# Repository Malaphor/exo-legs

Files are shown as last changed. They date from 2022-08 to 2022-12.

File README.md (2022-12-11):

# The Exoskeleton Project

## Overview

This project is a lower limb exoskeleton with 6 active joints. Its built with 3D printed and off-the-shelf parts. The aim is to get a basic, robust platform up and running for a comparatively low cost so that anyone that wants to can build it, use it and modify it however they wish. The exoskeleton is controlled with a [Teensy 4](https://www.pjrc.com/teensy/) and [ODrive 3.6](https://odriverobotics.com/shop/odrive-v36).

Requires [ODriveTeensyCAN](https://github.com/Malaphor/ODriveTeensyCAN) and [FlexCAN_T4](https://github.com/tonton81/FlexCAN_T4).

## Building

In the Documentation folder you will find assembly instructions and reference material for each of the parts required to build this project. There are separate folders for CAD files and STL files. The STL files are ready to print while the CAD files are there if you wish to modify any of the parts. Some off-the-shelf parts will need to be modified or adjusted to fit. For example, you may need to sand the inside of a bearing to fit around a motor or cut the aluminum extrusion to a specific length.

## Code

There are 3 subfolders in the Code folder. The code that runs on the Teensy is the brains of the exoskeleton. It handles gait, communication with motor controllers and sensors and also transfers data to the GUI. There is modified ODrive firmware that you'll need to flash to your ODrives to get voltage feedback from each joint potentiometer and to read some of the error flags in the heartbeat CAN message. Finally, the 3rd folder contains code for the GUI. This part is written in [Processing](https://processing.org/) and meant to be portable to run on whichever system you're using to control the exoskeleton, whether it be a tablet or desktop or something else.

# Mechanical Design

There are 6 active joints, 1 for each hip, knee and ankle. All of the joint actuators are designed to be extremely similar so once you get one joint working you can just print 5 more. The motor used here is a GARTT ML5210 brushless DC motor coupled to a size 17 120:1 strain wave gear (this is the most expensive part). This pair allows for up to 35Nm nominal torque and much more instantaneous torque. Both motor and gear are supported by large deep groove ball bearings and sandwiched between 3D printed parts. Between each joint and around the lower back are pieces of 20x40 aluminum extrusion that have been cut to length.

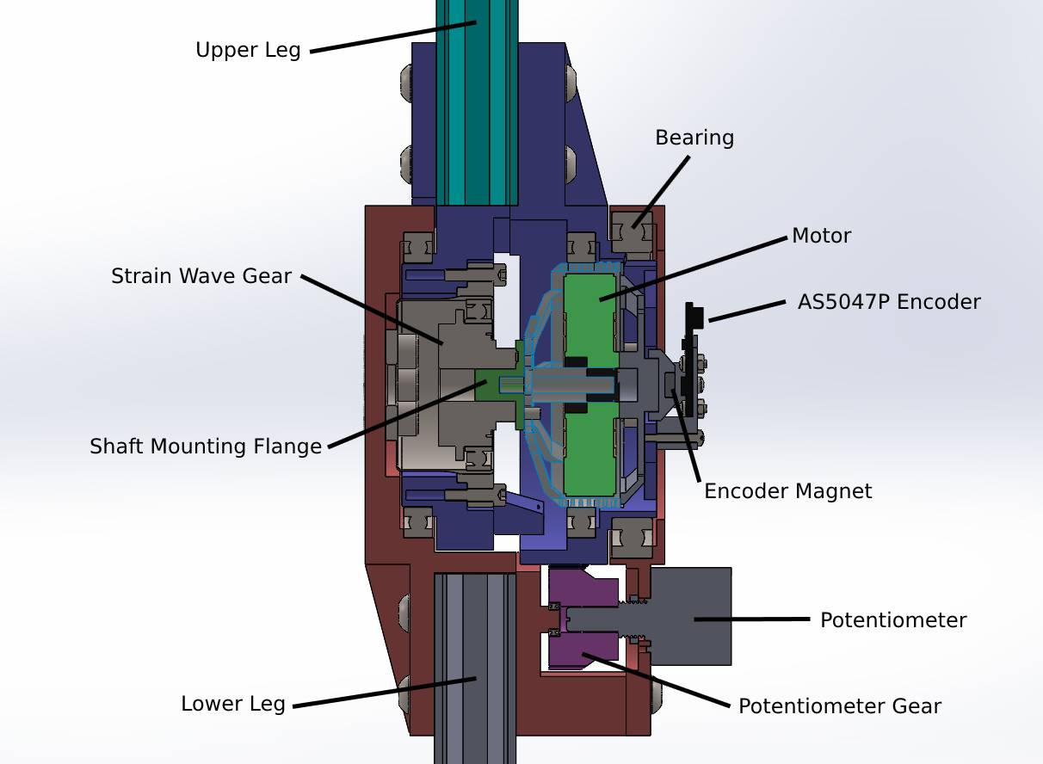
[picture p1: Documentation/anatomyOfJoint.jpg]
Anatomy of a Joint


# Electronics

A Teensy 4 MCU controls 3 v3.6 24V ODrives with a [SN65HVD230](https://www.ti.com/product/SN65HVD230) CAN transciever break out board operating at 1Mbps for communicating between them. Each ODrive controls 2 motors with an AS5047P eval board in ABI mode for motor commutation. An NTC 3950 thermistor was attached to the motor stator with thermal epoxy and wired into the ODrive to prevent overheating. The output of each joint also has a 3-turn potentiometer ([3547S-1AA-103A](https://www.mouser.com/datasheet/2/54/3547-776151.pdf)) that measures the joint position with voltage feedback from 0V (min angle) to 3.3V (max angle). Motor position given by the AS5047P multiplied by the gear ratio gives joint position for the gait while the potentiometer is used for getting the startup position and homing each of the joints. Power to the system is currently supplied by a generic PSU like that you might find on a 3D printer.

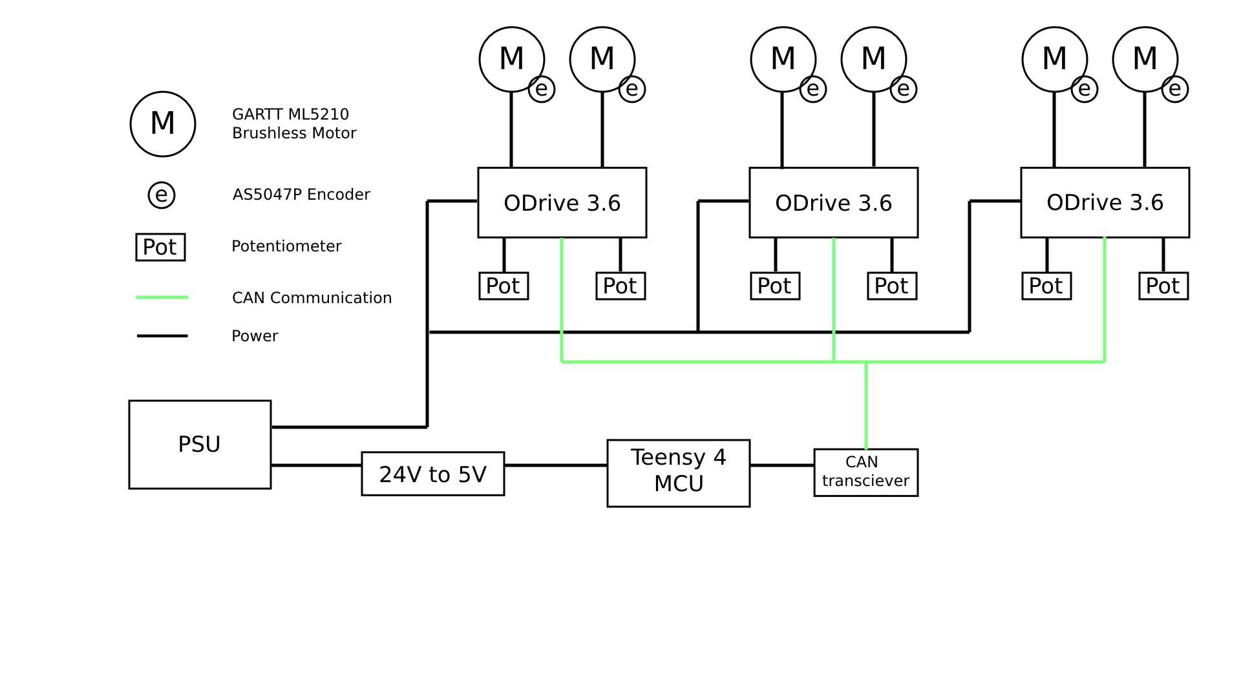
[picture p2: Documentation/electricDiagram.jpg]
Electric Diagram


*Note: If you're connecting an ODrive or Teensy to a PC a USB isolator is recommended

# Software

The initial control strategy is meant to be pretty straightforward. For each joint there's an array of 50 data points (from The Biomechanics and Motor Control of Human Gait, Winter 1987) that get looped through and sent to the ODrives as position commands. Sending these data points to the ODrive in position control results in choppy motion so filtered position control, command scheduling and cubic spline interpolation is used to smooth out the motion. An Arduino library called [Cubic Spline](https://github.com/avanderg/CubicSpline) handles the interpolation while the ODrive firmware filters the position commands sent from the Teensy at 100Hz. An online tool for visualizing cubic spline interpolation with an explanation of the math behind it can be found [here](https://tools.timodenk.com/cubic-spline-interpolation).

There's a separate header and implementation file that defines a Joint object which is used to keep track of various data related to each hip, knee and ankle joint. A section of the code is dedicated to reading CAN messages from the ODrives with the help of the ODriveTeensyCAN library. Data transfer between the Teensy and a PC is split into 2 types: GUI and not GUI (controlled by a variable definition). When in GUI mode data and commands are sent back and forth between the Teensy and the GUI. Otherwise you may use the Arduino console to input commands and read debug info. The code is well commented to make it easier to follow along.

## GUI

The GUI is meant to stream data from the Teensy and display information such as each joint position, speed and torque as well as give the user control over their movement.

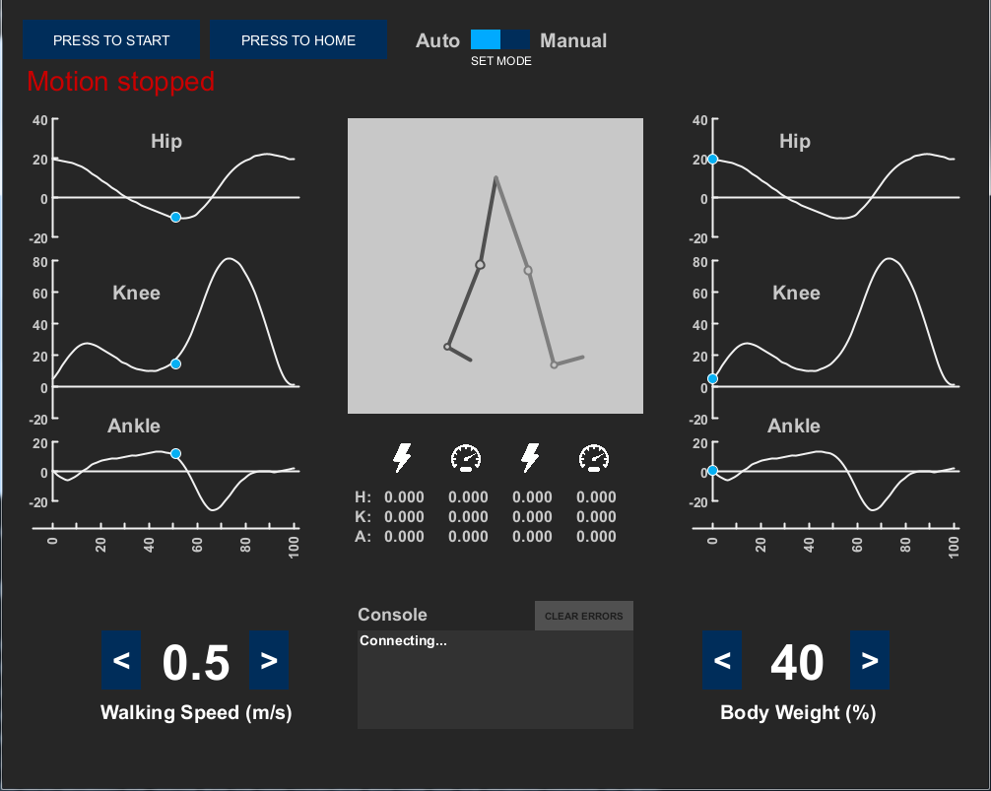
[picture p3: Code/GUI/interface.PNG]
Exoskeleton GUI


The buttons at the top can start, stop and home all of the joints. Graphs to either side display real time position data of each joint and the pair of legs between the graphs are animated to show the gait. Below the animated gait is a table that shows angular velocity and torque. The user can increase or decrease walking speed and how much body weight is supported by their own legs versus how much is supported by the lift. Lastly, a console is provided to show debug information such as errors from the motor controllers, the Teensy or if communication gets interrupted.

# TODO

- ~~Smooth jittery joint motion~~
- Update Teensy code to use threads/tasks
- Adapt joint design for ankle/footplate
- Review wiring for ground loops and isolation
- Locking connectors for everything
- Adjustable leg lengths
- Wiring instructions
- Assembly instructions

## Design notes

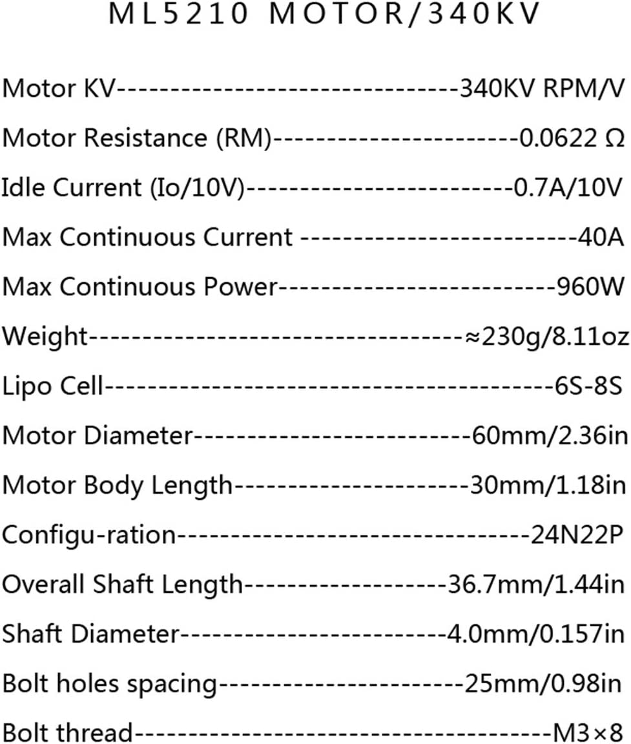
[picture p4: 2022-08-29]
Documentation/ML5210specs.jpg

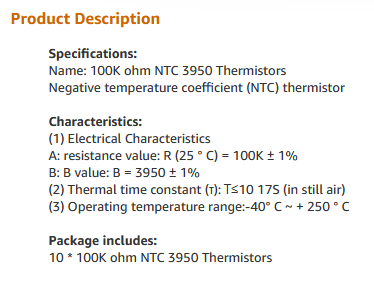
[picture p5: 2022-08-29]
Documentation/thermistorSpecs.PNG

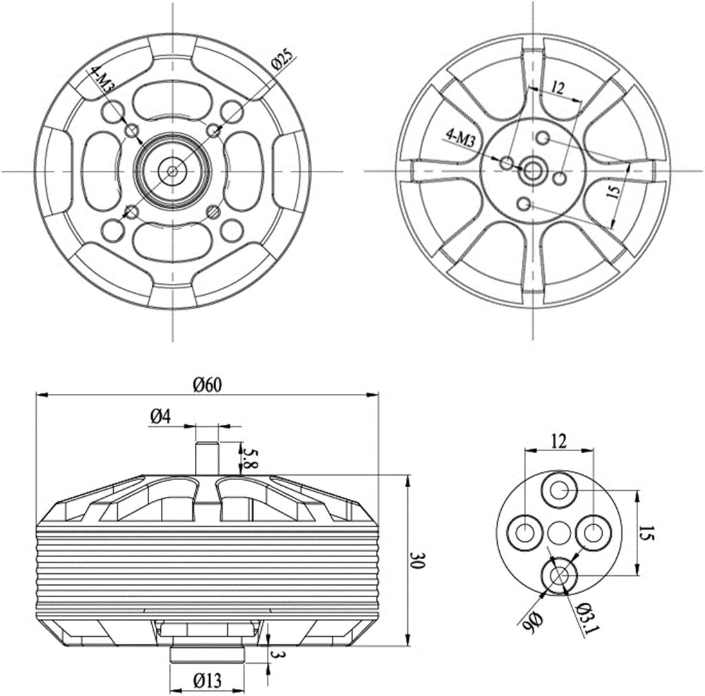
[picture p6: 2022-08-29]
Documentation/ML5210dims.jpg

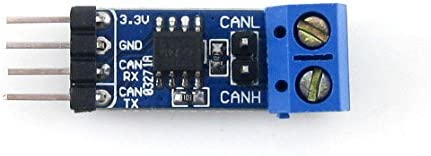
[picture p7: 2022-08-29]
Documentation/sn65hvd230CANmodule.jpg

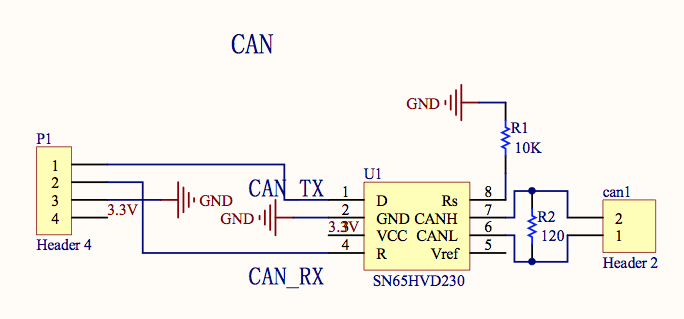
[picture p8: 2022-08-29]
Documentation/sn65hvd230CANmoduleCircuitDiagram.png

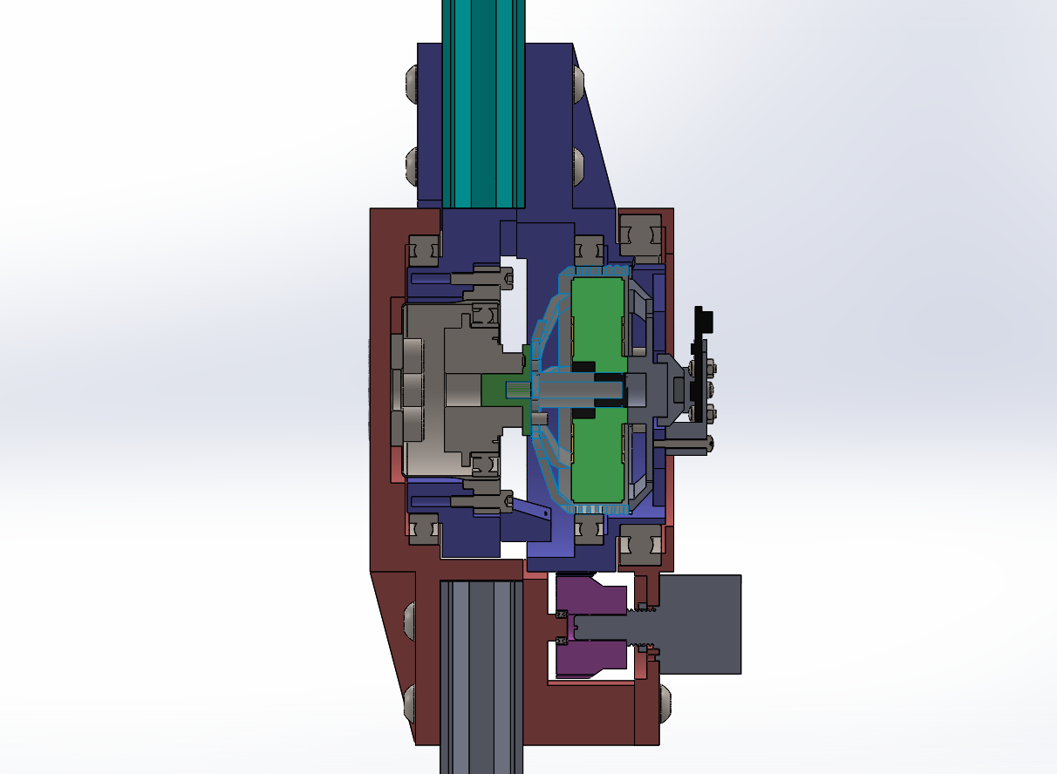
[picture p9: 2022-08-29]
Documentation/anatomyOfJoint.PNG

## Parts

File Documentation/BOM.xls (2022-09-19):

Item No. | Part Number | Description | Qty. | Note | Cost Each | Cost Total | Cost for 6 Joints
1 | gearHousing | Gear support and mount | 1
2 | csf-17-120-2a-r | Harmonic drive, size 17, 120:1 gear ratio | 1 |  | $375.00 | $375.00
3 | lowerLeg | 20x40 AL extrusion, cut to length | 1 | Needs to be cut | $9.99 | $9.99
4 | motor5210 | ML5210 BLDC motor | 1 |  | $44.99 | $44.99
5 | 6712-ZZ Bearing | 60x75x7 deep groove ball bearing | 2 | 1 needs to be sanded | $3.75 | $7.50
6 | 61813-ZZ Bearing | 65x85x10 deep groove ball bearing | 1 |  | $2.86 | $2.86
7 | MR85-ZZ Bearing | 5x8x2.5 deep groove ball bearing | 1 |  | $0.90 | $0.90
8 | upperLeg | 20x40 AL extrusion, cut to length | 1 | Needs to be cut | $9.99 | $9.99
9 | motorHousing | Motor support and mount | 1 |  |  | 0
10 | gearOutput | Attached to gear output | 1 |  |  | 0
11 | shaftMountingFlange | Interface between motor and gear | 1 | Might need to be machined |  | 0
12 | magnetHolder | Holds magnet onto back of motor rotor | 1 |  |  | 0
13 | Magnet | Diametric magnet for encoder | 1 | Comes with AS5047P eval board | $0.00 | $0.00
14 | AS5047P | Magnetic encoder eval board for motor commutation | 1 | Headers/wires need to be soldered | $16.76 | $16.76
15 | encoderHolder | Mounts encoder over center of magnet | 1 |  |  | 0
16 | potentiometerGear | Gear that attaches to potentiometer shaft | 1 |  |  | 0
17 | bournsPot | 3547S-1AA-103A 3 turn potentiometer | 1 |  | $30.80 | $30.80
18 | upperSupportMotor | Sits on motor housing, mounts potentiometer | 1 |  |  | 0
19 | potBracket | Supports upperSupportMotor and bearing for potentiometerGear | 1 |  |  | 0
20 | Tnut | M5 tnut for all screws holding pieces to AL extrusions | 24 |  | $0.06 | $1.44
21 | M5x10 SBHCS | M5 screw for AL extrusion | 16 | SBHCS = Socket Button Head Cap Screw | $0.16 | $2.56
22 | M5x16 SBHCS | M5 screw for AL extrusion | 4 |  | $0.19 | $0.76
23 | M5x40 SBHCS | M5 screw for AL extrusion | 2 |  | $0.29 | $0.58
24 | M3x8 SBHCS | M3 screw connecting motorHousing and gearHousing | 2 |  | $0.07 | $0.14
25 | M5x10 FHMS | Screws holding potBracket to AL extrusion under potentiometerGear | 2 | FHMS = Flat Head Machine Screw | $0.18 | $0.36
26 | M3x8 FHMS | Screws holding motor to motorHousing | 4 |  | $0.07 | $0.28
27 | M3x6 FHMS | Screws holding shaftMountingFlange to motor rotor | 2 |  | $0.07 | $0.14
28 | M3 Hex Nut | For screw holding potentiometerGear to potentiometer shaft | 1 |  | $0.07 | $0.07
29 | M2 Hex Nut | Nuts for screws holding AS5047P to encoderHolder | 4 |  | $0.07 | $0.28
30 | M3x8 Set Screw | Screw holding potentiometerGear to potentiometer shaft | 1 |  | $0.15 | $0.15
31 | M3x12 SHCS | Screws mounting circular spline of gear to gearHousing | 4 | 4 for now, up to 12 possible | $0.08 | $0.32
32 | M5x8 SHCS | Secure gear output (flex spline) to gearOutput | 6 | SHCS = Socket Head Cap Screw | $0.15 | $0.90
33 | M5 Hex Jam Nut | Secure gear output to gearOutput. Thinner than standard hex nut | 6 |  | $0.08 | $0.48
34 | M2x5 PHMS | Holds AS5047P to encoderHolder | 4 | PHMS = Pan Head Machine Screw | $0.07 | $0.28
35 | M2x13 PHMS | Holds encoderHolder to motorHousing | 3 | Might change to M3x12 or M3x14 | $0.08 | $0.24
36 | potentiometerNut | Secures bournsPot to upperMotorSupport | 1 | Comes with potentiometer | $0.00 | $0.00
 |  |  |  |  |  |  |  | Add shipping
 |  | POLYPROPYLENE

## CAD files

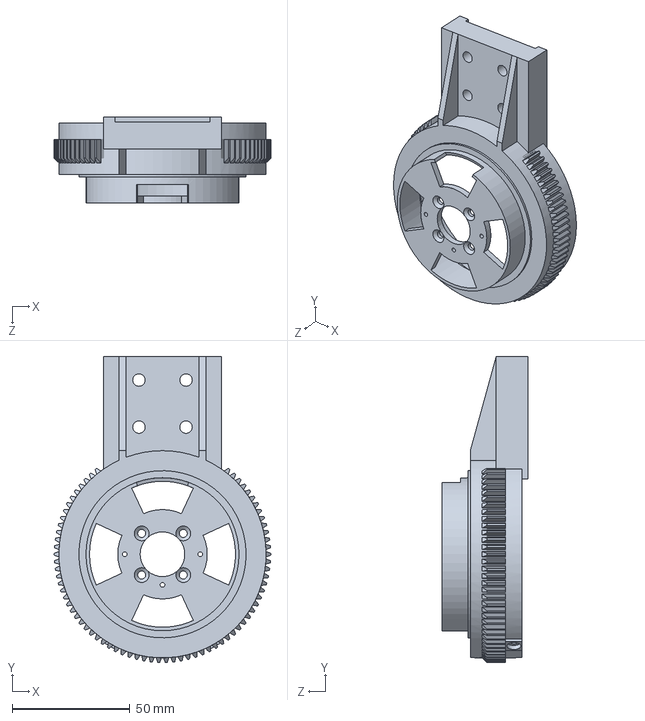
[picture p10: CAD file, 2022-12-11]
Documentation/CAD/motorHousing.SLDPRT
92.0 x 130.0 x 36.5 mm

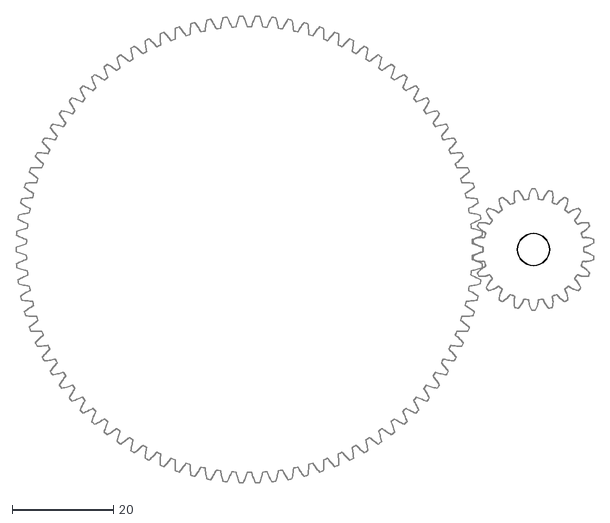
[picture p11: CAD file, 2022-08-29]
Documentation/involuteGearProfile.dxf
113.9 x 92.0

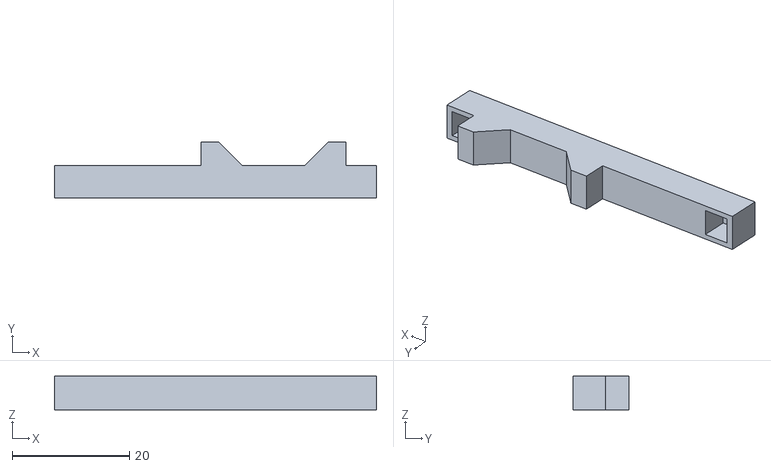
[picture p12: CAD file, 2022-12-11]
Documentation/STL/nutHelper.STL
55.0 x 9.60 x 5.80

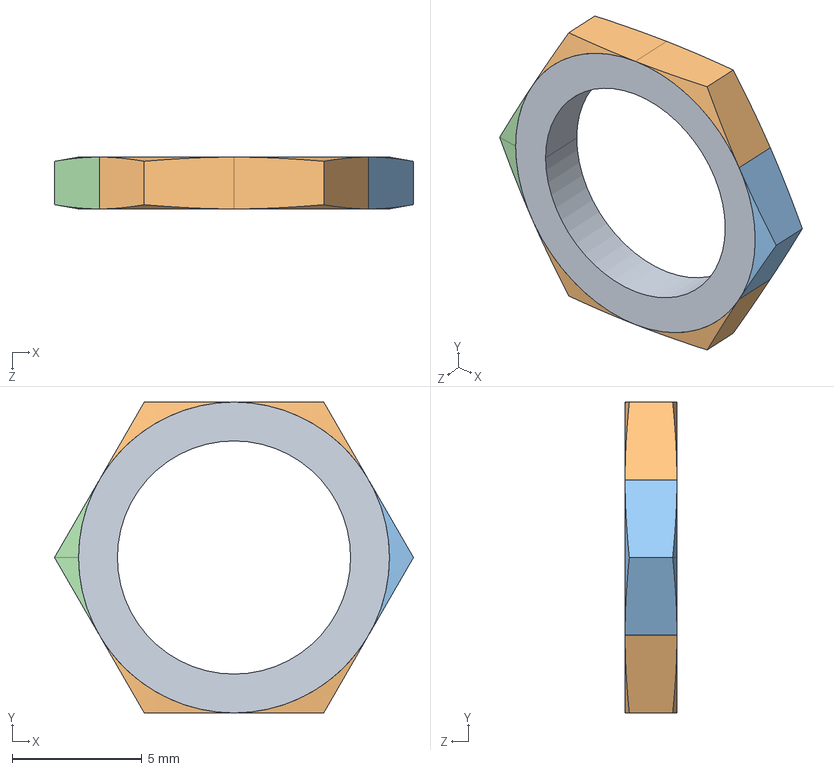
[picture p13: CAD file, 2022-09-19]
Documentation/CAD/potentiometerNut.STEP
13.9 x 12.0 x 2.00 mm

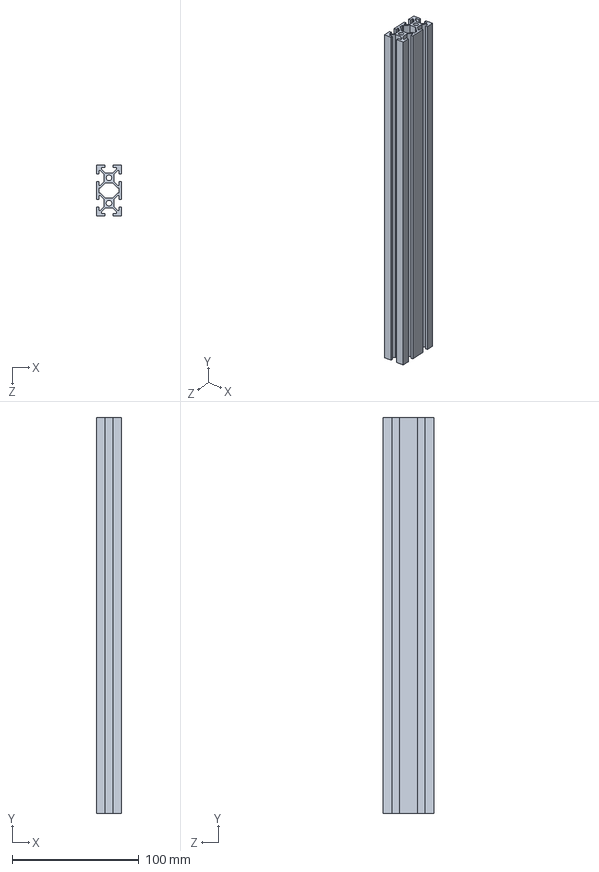
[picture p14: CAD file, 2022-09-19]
Documentation/CAD/lowerLeg.SLDPRT
20.0 x 313.0 x 40.0 mm

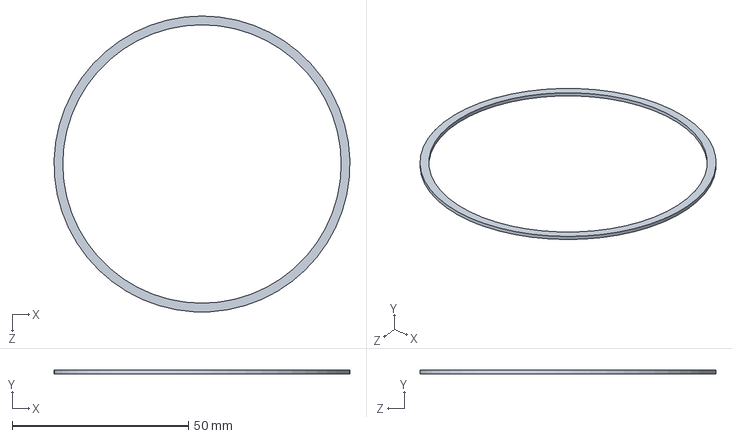
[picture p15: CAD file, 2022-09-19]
Documentation/CAD/ring.SLDPRT
84.0 x 1.00 x 84.0 mm

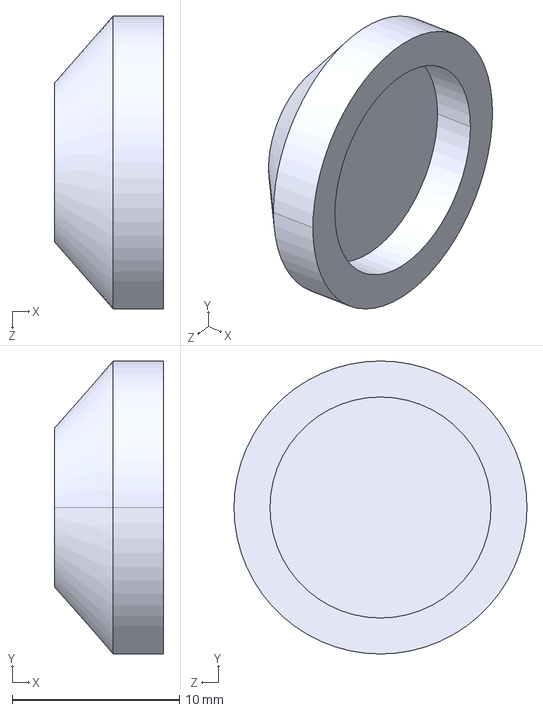
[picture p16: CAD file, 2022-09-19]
Documentation/CAD/magnetHolder.STEP
6.50 x 17.5 x 17.5 mm

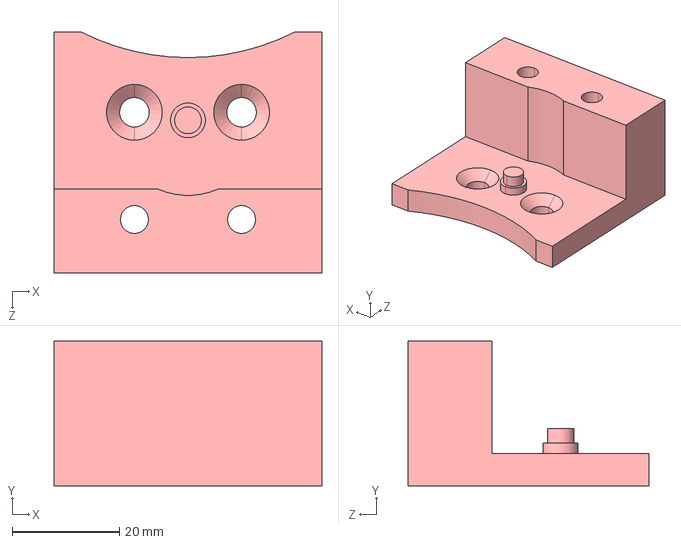
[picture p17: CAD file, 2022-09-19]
Documentation/CAD/potBracket.STEP
50.0 x 27.0 x 45.0 mm

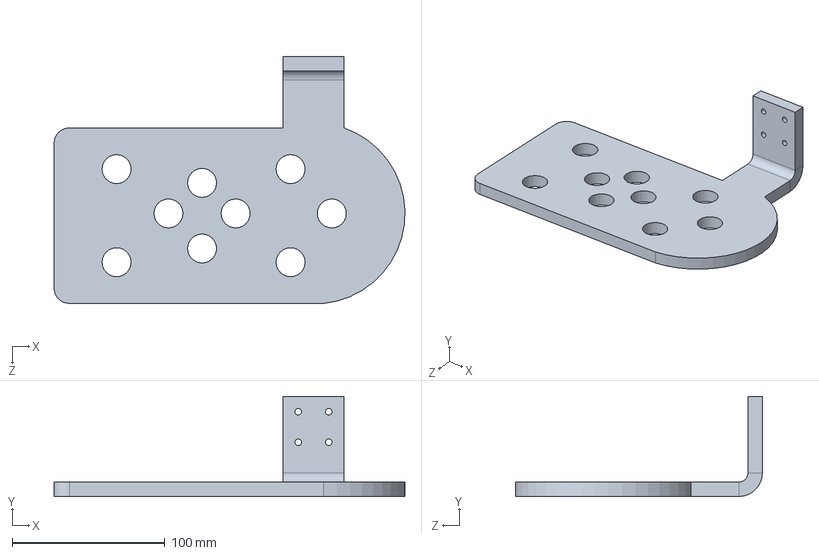
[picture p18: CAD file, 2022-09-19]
Documentation/CAD/footPlateRight.SLDPRT
230.0 x 65.6 x 161.8 mm

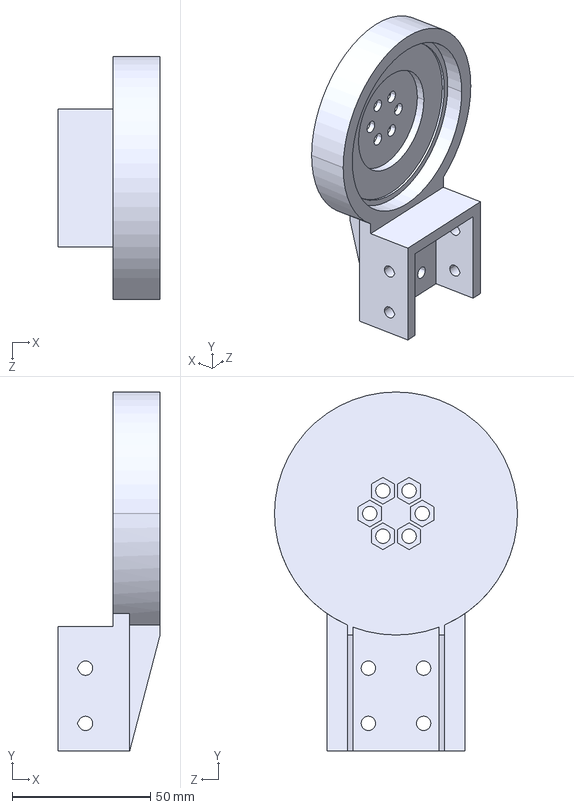
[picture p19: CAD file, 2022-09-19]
Documentation/CAD/gearOutput.STEP
37.0 x 130.0 x 88.0 mm

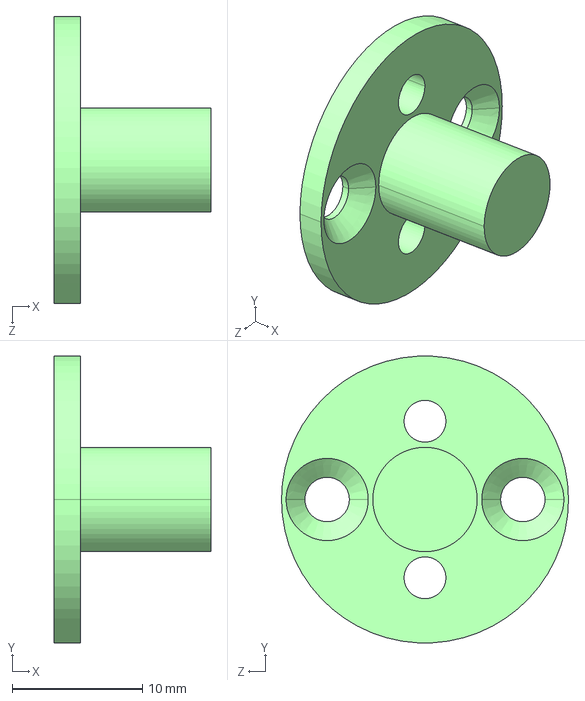
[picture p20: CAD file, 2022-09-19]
Documentation/CAD/shaftMountingFlange.STEP
12.0 x 22.0 x 22.0 mm

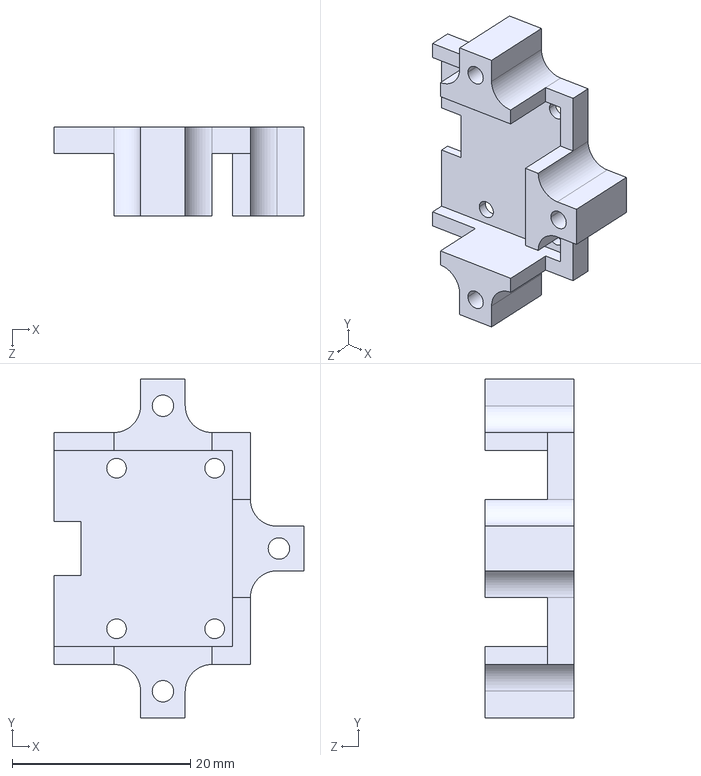
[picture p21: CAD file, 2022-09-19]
Documentation/CAD/encoderHolder.STEP
28.0 x 38.0 x 10.0 mm

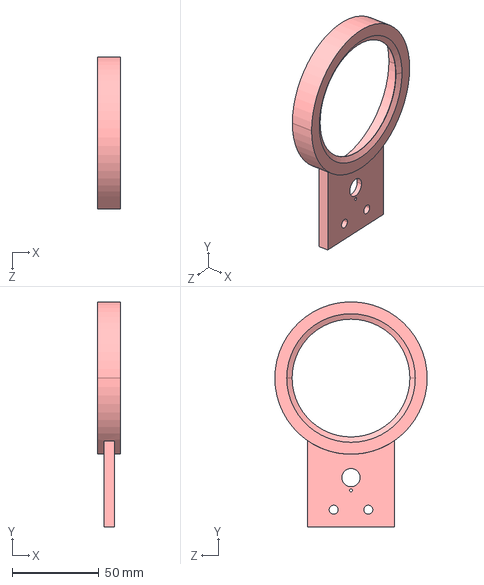
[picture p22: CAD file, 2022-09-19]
Documentation/CAD/upperSupportMotor.STEP
13.5 x 129.9 x 88.0 mm

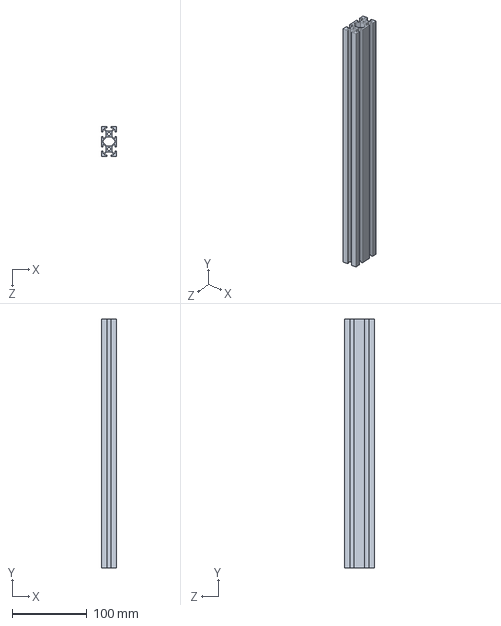
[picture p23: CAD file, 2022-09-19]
Documentation/CAD/upperLeg.SLDPRT
20.0 x 332.0 x 40.0 mm

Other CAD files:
Documentation/CAD/potentiometerGear.STEP
Documentation/CAD/gearHousing.STEP
Documentation/CAD/AS5047P.STEP
Documentation/CAD/bournsPot.STEP
Documentation/CAD/61813bearing.STEP
Documentation/CAD/6712bearing.STEP
Documentation/CAD/MOTOR5210.STEP
Documentation/CAD/MR85bearing.STEP
Documentation/CAD/bearingHelper.STEP
Documentation/CAD/csf-17-120-2a-r.STEP
Documentation/CAD/encoderHolder.SLDPRT
Documentation/CAD/gearHousing.SLDPRT
Documentation/CAD/gearOutput.SLDPRT
Documentation/CAD/magnet.STEP
Documentation/CAD/magnetHolder.SLDPRT
Documentation/CAD/potBracket.SLDPRT
Documentation/CAD/potentiometerGear.SLDPRT
Documentation/CAD/shaftMountingFlange.SLDPRT
Documentation/CAD/upperSupportMotor.SLDPRT
Documentation/STL/bearingHelper.STL
Documentation/STL/gearOutput.STL
Documentation/STL/motorHousing.STL
Documentation/STL/potBracket.STL
Documentation/STL/ring.STL
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

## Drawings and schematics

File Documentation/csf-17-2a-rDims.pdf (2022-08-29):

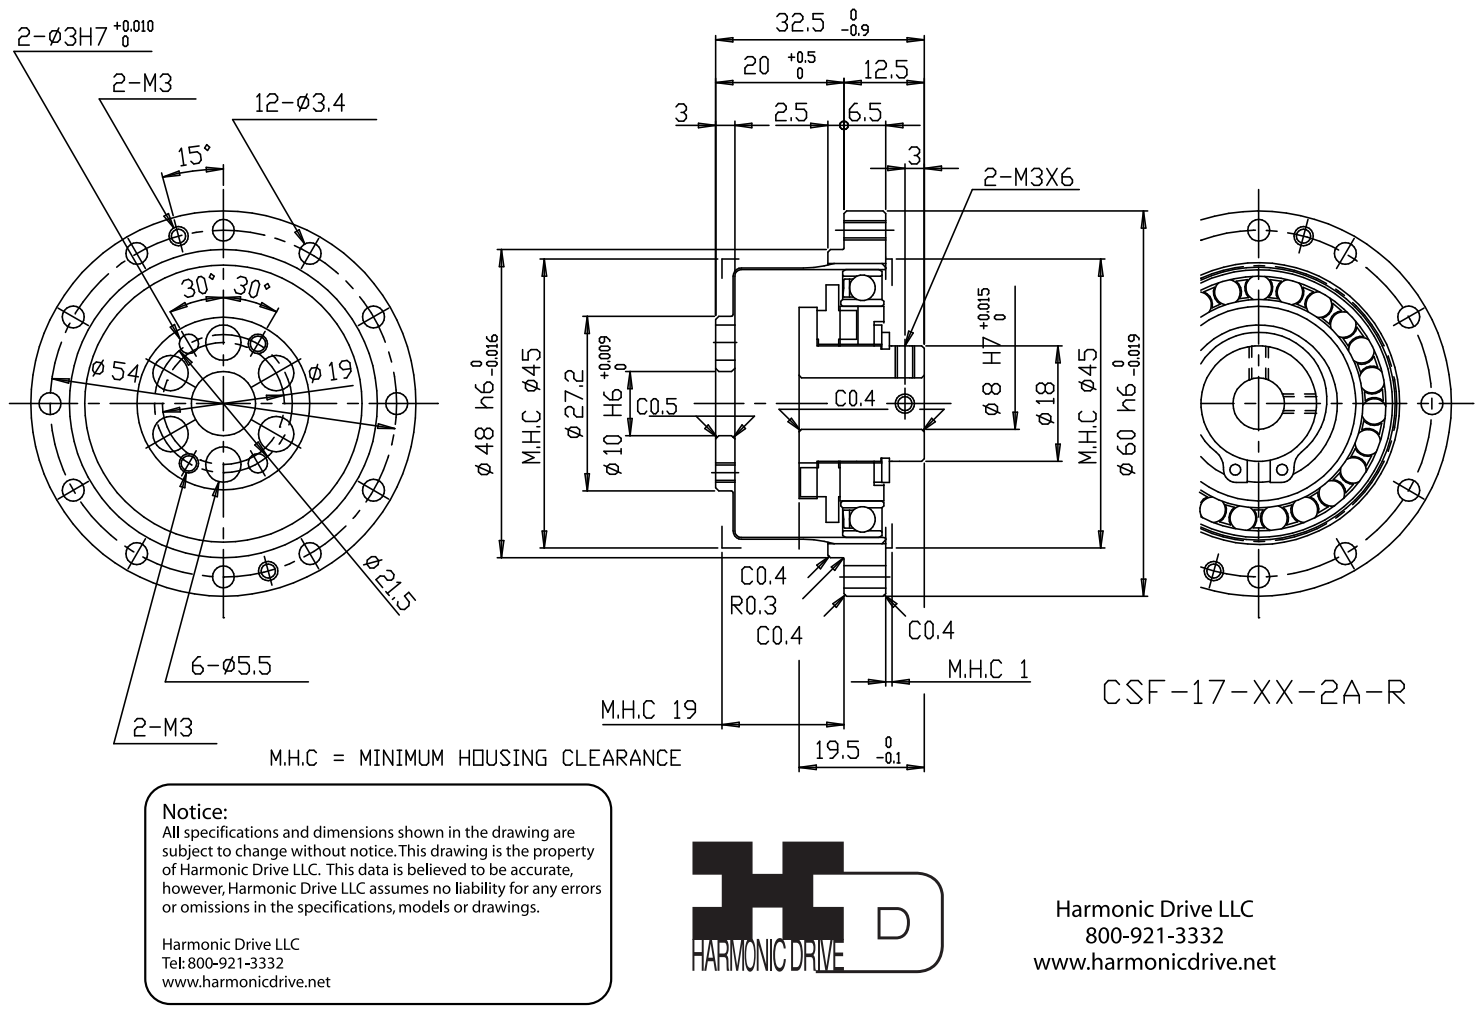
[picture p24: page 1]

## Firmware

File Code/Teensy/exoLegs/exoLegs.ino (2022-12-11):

#include <cube_spline.h>
#include <FlexCAN_T4.h>
#include <ODriveTeensyCAN.h>
#include "Joint.h"


// Printing with stream operator
template<class T> inline Print& operator <<(Print &obj,     T arg) { obj.print(arg);    return obj; }
template<>        inline Print& operator <<(Print &obj, float arg) { obj.print(arg, 4); return obj; }

//read only and #define
#define DEBUG
//#define GUI
//these are now pins on odrive
#define rightPosPinHip 5  //pin to read pot val for hip pos
#define rightPosPinKnee 4  //pin to read pot val for knee pos
#define rightPosPinAnkle 5  //pin to read pot val for ankle pos
#define leftPosPinHip 6  //pin to read pot val for hip pos
#define leftPosPinKnee 5  //pin to read pot val for knee pos
#define leftPosPinAnkle 4  //pin to read pot val for ankle pos

//const float potValToDeg = 0.009;  //convert pot voltage to degrees
const float homePotVal = 1.62;  //value of joint pot when joint angle == 0, in volts
const int rightHipOffset = 0;  //pot voltage when hip is at 0deg
const int rightKneeOffset = 1.71;  //pot voltage when knee is at 0deg
const int rightAnkleOffset = 459;  //pot voltage when ankle is at 0deg
const int leftHipOffset = 0;  //pot voltage when hip is at 0deg
const int leftKneeOffset = 989;  //pot voltage when knee is at 0deg
const int leftAnkleOffset = 459;  //pot voltage when ankle is at 0deg
const float posDiffThreshold = 0.01;  //0.02how close to target voltage before its ready, in volts or revs
const float motorCurrentLimit = 15.0;  //max motor current
const int numJoints = 1;  //number of active joints, used for testing

const float stateChangeTime = 1.0 / 799.0;  //time to wait for odrive axis to change states
int led = 13;  //onboard led pin
int ledState = LOW;  //LOW = off. Keep track of LED state

//program advancement variables
bool programRunning = false;  //is program running?
int leftLegTarget = 0;  //start array index for left leg joints -------------------- CAHNGE BACK TO 24 -----------------
int rightLegTarget = 0;  //start array index for right leg joints
bool allJointsReady = false;  //are all joints at target angle?
bool allJointsHomed = false;  //homing sequence completed for all joints
unsigned long sendCmdInterval = 0;

//serial reading
char inBytes[32];  //array to read in commands via serial, could probably be smaller
bool doneReading = false;  //finished reading cmd via serial?
float inVal = 0;  //manual pos cmd via serial. Not implemented
String optionString = "Options: <x> to clear errors, <c1> to calibrate axis1, <h> to home joints, <p> to start position, <r> to run program, <s> to stop";

//data transfer
String dataToSend = "";  //string of data values to send to gui
String errorString = "";  //string of all current errors to send to gui
unsigned long contactTimer = 0;

//speed & weight variables
float segTime = 0.08;  //0.0314;  //0.0314 time in sec between angle datapoints, affects walk speed
float weight = 53.0;  //body weight in kg, measured by current draw
float bodyWeight = 50.0;  //% body weight supported by lift

//error variables
uint64_t errorVals[3] = {0, 0, 0};  //initialize errors to 0, no errors
uint32_t axisError = 0;  //32bit axis error
uint64_t motorError = 0;  //64bit motor error
uint32_t encoderError = 0;  //32bit encoder error
uint32_t currentState = 1;  //1 == IDLE
bool isError = false;  //is there currently an error?

unsigned long canMsgTimeout = 0;  //used to wait for CAN message response

//cubic spline interpolation
S output;  //struct
S *output_ptr = NULL;  //pointer to struct
int num_angles = 52;  //needed for cubic spline input
float csVal = 0;  //val to be interpolated in sec after start of gait
float csResult = 0;  //output of interpolater, arg of joint->SetPosition()
int csError = 0;  //checks if value is in domain of dataset
unsigned long startGaitTime = 0;  //time when gait starts in millis()
float endGaitTime = segTime * (num_angles - 1) - 0.01;  //total time for gait in sec
float currentGaitTime = 0;  //time after start of gait in sec
bool restartGait = true;  //if reached end of gait, restart
float csXVals[52] = {};  //segTime vals corresponding to joint angles

//positive angle is flexion, negative is extension
float hipAngles[52] = {19.33, 18.92, 18.45, 17.94, 17.3, 16.4, 15.18, 13.67, 11.97, 10.21, 8.48, 6.74, 4.94, 3.13, 1.42,
                     -0.13, -1.54, -2.87, -4.12, -5.3, -6.4, -7.43, -8.39, -9.27, -10.02, -10.61, -10.95, -10.91, -10.31,
                     -9.0, -6.95, -4.25, -1.05, 2.42, 5.93, 9.22, 12.11, 14.55, 16.53, 18.13, 19.45, 20.54, 21.38, 21.84,
                     21.87, 21.5, 20.84, 20.09, 19.5, 19.18, 19.01, 19.5
                    };
float kneeAngles[52] = {3.97, 7.0, 10.52, 14.12, 17.38, 19.84, 21.27, 21.67, 21.22, 20.20, 18.86, 17.35, 15.73, 14.08, 12.5,
                      11.09, 9.91, 8.97, 8.28, 7.86, 7.72, 7.94, 8.6, 9.76, 11.5, 13.86, 16.97, 20.96, 26.0, 32.03, 38.74,
                      45.6, 52.05, 57.54, 61.66, 64.12, 64.86, 63.95, 61.59, 57.97, 53.27, 47.58, 40.94, 33.46, 25.38,
                      17.27, 9.94, 4.31, 1.12, 0.54, 2.21, 4
                     };
float ankleAngles[51] = {0.02, -2.06, -3.88, -4.6, -3.98, -2.4, -0.45, 1.45, 3.04, 4.27, 5.13, 5.71, 6.1, 6.43, 6.76, 7.12,
                       7.54, 7.99, 8.44, 8.86, 9.23, 9.51, 9.62, 9.43, 8.7, 7.2, 4.69, 1.15, -3.26, -8.17, -13.05, -17.13,
                       -19.52, -19.77, -18.12, -15.29, -12.04, -8.85, -5.96, -3.51, -1.64, -0.5, -0.07, -0.16, -0.42, -0.52,
                       -0.26, 0.36, 1.0, 1.2, 0.58
                      };
float *hipAnglesPtr = hipAngles;  //pointer to float array
float *kneeAnglesPtr = kneeAngles;  //pointer to float array
float *ankleAnglesPtr = ankleAngles;  //pointer to float array


ODriveTeensyCAN odriveCAN(1000000);  //CAN bus object initialized with speed of 1Mbps
ODriveTeensyCAN *odriveCANPtr = &odriveCAN;  //pointer to CAN bus object
CAN_message_t inMsg;  //incoming CAN message
HeartbeatMsg_t returnVals;  //struct that holds heartbeat message data
EncoderEstimatesMsg_t encoderEstimates;  //struct that holds encoder data
IqMsg_t iqVals;  //struct that holds current setpoint and measured current

//joint objects ---------------------------change kneeAnglesPtr
Joint leftKnee(0, leftPosPinKnee, leftKneeOffset, hipAnglesPtr, leftLegTarget, odriveCANPtr);  //CAN node_id, potPin, offset, angles array, leg starting target, CANbus
Joint leftAnkle(1, leftPosPinAnkle, leftAnkleOffset, ankleAnglesPtr, leftLegTarget, odriveCANPtr);
Joint rightKnee(2, rightPosPinKnee, rightKneeOffset, kneeAnglesPtr, rightLegTarget, odriveCANPtr);
Joint rightAnkle(3, rightPosPinAnkle, rightAnkleOffset, ankleAnglesPtr, rightLegTarget, odriveCANPtr);
Joint leftHip(4, leftPosPinHip, leftHipOffset, hipAnglesPtr, leftLegTarget, odriveCANPtr);
Joint rightHip(5, rightPosPinHip, rightHipOffset, hipAnglesPtr, rightLegTarget, odriveCANPtr);

//pointers to joint objects
Joint *leftKneeR = &leftKnee;
Joint *leftAnkleR = &leftAnkle;
Joint *rightKneeR = &rightKnee;
Joint *rightAnkleR = &rightAnkle;
Joint *leftHipR = &leftHip;
Joint *rightHipR = &rightHip;

Joint *allJoints[] = {leftKneeR, leftAnkleR, rightKneeR, rightAnkleR, leftHipR, rightHipR};  //array of pointers to joint objects for looping

//names corresponding to joint objects. Must be in the same order as allJoints[]. For error reporting/debug
const char *jointNames[] = {"Left knee", "Left ankle", "Right knee", "Right ankle", "Left hip", "Right hip"};  


void setup() {
  // put your setup code here, to run once:
  Serial.begin(115200);  //start Serial monitor
  pinMode(led, OUTPUT);  //led pin as output
  digitalWrite(led, HIGH);  //turn on led
  ledState = HIGH;  //update LED state

  contactTimer = millis();
  while(!Serial) {
    //wait for computer serial connection
    if(millis() - contactTimer > 5000) {
      break;
    }
  }
  delay(100);  //brief pause

  #ifdef DEBUG  //debug var to help see code stages
    Serial.println("Waiting for heartbeat");
    for(int i = 0;i < numJoints;i++) {  //step through array of joints
      //Serial << odriveCAN.Heartbeat() << '\n';  //rewrite to wait for specific heartbeat
    }
  #endif
  
  do {  //do this first
    if(odriveCAN.ReadMsg(inMsg)) {  //if theres a message on the CAN bus
      uint32_t axis_id = inMsg.id >> 6;  //get axis id
      uint8_t cmd_id = inMsg.id & 0x01F;  //get command id
      if(cmd_id == ODriveTeensyCAN::CMD_ID_ODRIVE_HEARTBEAT_MESSAGE) {  //if command id is for heartbeat message
        handleCANMsg(axis_id, inMsg, allJoints[axis_id]);  //take care of it
        break;  //exit do while loop
      }  //end if
    }  //end do
  } while(millis() - canMsgTimeout < 2000);  //only loop for 2sec

  delay(100);  //brief pause
  /*for(int i = 0;i < numJoints;i++) {  //step through array of joints
    allJoints[i]->ClosedLoopCtrl();  //put joint into closed loop control
    delay(stateChangeTime);  //8kHz ctrl loop on odrive. Pause for 1 ctrl loop to give joint enough time to enter closed loop control
    
    if(allJoints[i]->GetCurrentState() == ODriveTeensyCAN::AXIS_STATE_CLOSED_LOOP_CONTROL) {  //check to see if joint actually made it into closed loop
      #ifdef GUI
        //do nothing
      #else
        Serial << jointNames[i] << " ready" << '\n';  //if yes, print that its ready
      #endif
    } else {
      #ifdef GUI
        checkJointErrors(allJoints[i]);  //check joint for errors
        if(isError) {  //if an error was found
          Serial << '<' << errorString << i << '>' << '\n';  //send errors + joint index wrapped in start/end chars
        }
      #else
        Serial << jointNames[i] << " failed to enter closed loop control" << '\n';  //if not, notify that it didnt
        checkJointErrors(allJoints[i]);  //check joint for errors, print them
      #endif
    }
    #ifdef GUI
      errorString = "< , , , ,6>";  //signal end of joint errors
      Serial << errorString << '\n';  //send it
    #endif
    delay(100);  //brief pause
  }*/

  fillSegTimeArray();  //fill array w/time vals corresponding to angles
  output.x = csXVals;  //initial x values
  output.y = ankleAngles;  //initial y values
  output_ptr = nat_cubic_spline(num_angles, &output);  //performs natural cubic spline of given dataset

  #ifdef GUI  //if using gui
    establishContact();  //handshake with gui comp
    sendData();  //send bool, pos, vel, current updates
  #else  //if using serial monitor
    Serial.println("Setup Complete");  //done trying to get all joints into closed loop control
    Serial.println(optionString);  //print available options for user to select
  #endif

  sendCmdInterval = millis();
}
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

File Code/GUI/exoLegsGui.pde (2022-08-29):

import controlP5.*;  //for graphics
import processing.serial.*;  //for serial comms with teensy via usb

Serial teensyPort;  //serial port object for usb comms with teensy
int teensyPortTimer = 0;  //how long since data recieved. checks port connection
int reconnectAttempts = 0;  //repeated failed attempts throws error
String[] serialValues = new String[22];  //data from serial split into strings
boolean[] serialBoolValues = new boolean[4];  // == {homed, programRunning, isError, allJointsReady}
String[] speedWeightValues = new String[2];  // == walkingSpeed, bodyWeightPercent
String[] errorString = new String[5];  // == {joint name, motorError, encoderError, axisError, index}
String fromTeensy;
char firstChar;
boolean handShake = false;  //contact with teensy
boolean firstContact = false;  //first time made serial connection
boolean homed = false;  //have all joints been homed
boolean moving = false;  //are legs moving
boolean modeSet = false;
boolean readyToAdvance = false;  //are all joints at target position and ready to move to next position
boolean oldErrorVal = false;  //was there previously an error?
boolean firstError = true;  //when recieving errors, is this the first one?
int timer = millis();
int updateTimer = 200;  //interval to update timer in ms

float motorKv = 340.0;  //motor kv

//array of angles for each leg joint
float[] hipAngles = {19.33, 18.92, 18.45, 17.94, 17.3, 16.4, 15.18, 13.67, 11.97, 10.21, 8.48, 6.74, 4.94, 3.13, 1.42,
                     -0.13, -1.54, -2.87, -4.12, -5.3, -6.4, -7.43, -8.39, -9.27, -10.02, -10.61, -10.95, -10.91, -10.31,
                     -9.0, -6.95, -4.25, -1.05, 2.42, 5.93, 9.22, 12.11, 14.55, 16.53, 18.13, 19.45, 20.54, 21.38, 21.84,
                     21.87, 21.5, 20.84, 20.09, 19.5, 19.18, 19.01
                    };
float[] kneeAngles = {3.97, 7.0, 10.52, 14.12, 17.38, 19.84, 21.27, 21.67, 21.22, 20.20, 18.86, 17.35, 15.73, 14.08, 12.5,
                      11.09, 9.91, 8.97, 8.28, 7.86, 7.72, 7.94, 8.6, 9.76, 11.5, 13.86, 16.97, 20.96, 26.0, 32.03, 38.74,
                      45.6, 52.05, 57.54, 61.66, 64.12, 64.86, 63.95, 61.59, 57.97, 53.27, 47.58, 40.94, 33.46, 25.38,
                      17.27, 9.94, 4.31, 1.12, 0.54, 2.21
                     };
float[] ankleAngles = {0.02, -2.06, -3.88, -4.6, -3.98, -2.4, -0.45, 1.45, 3.04, 4.27, 5.13, 5.71, 6.1, 6.43, 6.76, 7.12,
                       7.54, 7.99, 8.44, 8.86, 9.23, 9.51, 9.62, 9.43, 8.7, 7.2, 4.69, 1.15, -3.26, -8.17, -13.05, -17.13,
                       -19.52, -19.77, -18.12, -15.29, -12.04, -8.85, -5.96, -3.51, -1.64, -0.5, -0.07, -0.16, -0.42, -0.52,
                       -0.26, 0.36, 1.0, 1.2, 0.58
                      };
                      
//variables for leg motion graphics
float hipX = 400;
float hipY = 180;
float legSegLength = 100;
float footSegLength = 30;

float convertPotToAngle = 6.7;  //NEW POT. CHECK THIS VALUE

float leftGraphsXPos;
float rightGraphsXPos;
int graphWidth = 250;
int leftLegGaitProgress = 50;
int rightLegGaitProgress = 0;

//variables to display joint info
float rightHipTorque = 0;
float rightKneeTorque = 0;
float rightAnkleTorque = 0;
float leftHipTorque = 0;
float leftKneeTorque = 0;
float leftAnkleTorque = 0;
float rightHipSpeed = 0;
float rightKneeSpeed = 0;
float rightAnkleSpeed = 0;
float leftHipSpeed = 0;
float leftKneeSpeed = 0;
float leftAnkleSpeed = 0;
float[] torque = {0, 0, 0, 0, 0, 0};
float[] speed = {0, 0, 0, 0, 0, 0};

float rightLegTarget;

//start angles for joints
float rightHipAngle = hipAngles[0];
float rightKneeAngle = kneeAngles[0];
float rightAnkleAngle = ankleAngles[0];
float leftHipAngle = hipAngles[24];
float leftKneeAngle = kneeAngles[24];
float leftAnkleAngle = ankleAngles[24];

float walkingSpeed = 0.5;
float walkSpeedLimitLow = 0.3;
float walkSpeedLimitHigh = 1.0;
int bodyWeightPercent = 40;  //percent supported. 10% to 80%?
int bodyWeightLimitLow = 10;
int bodyWeightLimitHigh = 80;

//images for graphic interface
PImage leftArrow;
PImage allJointImg;
PImage currentSymbol;
PImage speedometer;
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

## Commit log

2020-09-30 update to use custom joint objects
2020-10-03 refactor code to make better use of joint object
2022-08-29 Update contents, file structure
    Updated code, readme, added docs, reference materials
    [BOM.ods]
2022-08-29 Update readme, add more file
    [csf-17-120-2a-r.STEP, involuteGearProfile.dxf]
2022-08-30 Add CAD files
    [61813bearing.STEP, 6712bearing.STEP, AS5047P.STEP, BOM.ods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]
2022-09-07 Updated teensy code to match updated odriveteensycan library
2022-09-19 Update CAD and STL files
    [BOM.xls, encoderHolder.SLDPRT, encoderHolder.STEP, footPlateRight.SLDPRT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]
2022-12-11 Update models & code
    New and updated CAD and STLs
    Stop jittery motion
    [gearHousing.SLDPRT, gearOutput.SLDPRT, gearOutput.STL, jointAnglesVelocities.xls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]
